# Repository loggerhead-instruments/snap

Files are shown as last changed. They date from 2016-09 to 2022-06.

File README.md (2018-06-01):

# SNAP
SNAP is an arduino-compatible audio datalogger board (designed for Teensy 3.x)

More information is at http://loggerhead.com

Files:
- snap: Main control and sensor recording
- cmd.pde: Reads recording settings from a script file
- wav.h: wav header
- rms: rms calculation

Software supports:
- duty cycle recording
- display
- button input for recording setup
- writing to microSD

## Updating Firmware

1.	Install Teensyduino from https://www.pjrc.com/teensy/loader.html
2.	Get latest hex file from appropriate repository
	https://github.com/loggerhead-instruments/snap/tree/master/hex
	To download the file, left-click on the file name, and then right click on the Raw button and select Save As link.
3.	Connect microUSB cable to small board on device. You may have to unscrew board.
4.	Run the Teensy Loader program.
5.	From File Menu, select Open HEX File
6.	Press the button on the board, or from Operation menu, select Program (you may have to turn off automatic mode).

To check whether the firmware has been updated, collect some data, and check the log files for the version date of the firmware.

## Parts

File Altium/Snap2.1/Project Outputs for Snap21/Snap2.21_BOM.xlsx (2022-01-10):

Comment | Description | DigiKey | Designator | Footprint | LibRef | Quantity | 100sets |  | NOTE
1uF | Ceramic Chip Capacitor - X7R, 1% |  | C1, C11, C16, C22 | 0402 | C0402 | 4 | $0.013 | $5.280
10uF | Tantalum Capacitor, 20%, 6.3V or better |  | C2, C6, C9, C14, C20 | Tant0805 | Tant0805 | 5 | $0.330 | $165.000 | TANT 10UF 6.3V 0805
0.1uF | Ceramic Chip Capacitor - X7R, 10% | 1276-1001-2-ND | C7, C8, C10, C13, C15, C17, C19, C21 | 0402 | C0402 | 8 | $0.013 | $10.560 | CL05B104KO5NNNC
0.01uF | Ceramic Chip Capacitor - X7R, 10% |  | C12, C18, C23 | 0402 | C0402 | 3 | $0.009 | $2.640
1.0uF | Ceramic Chip Capacitor - X7R, 1% |  | C24, C25, C26 | 0402 | C0402 | 3 | $0.013 | $3.960
LED_0603 | SML-D12M1WT86 or similar green | SML-D12M1WT86TR-ND | D1 | Diode0603 | LED_0603 | 1 | $0.121 | $12.100 | SML-D12M1WT86 5-7work days
Header 2 | 705530036 |  | P2 | HDR1X2 | Header 2 | 1 | $1.122 | $112.200 | 5-7work days
CoinCellHolder | BU2032SM-BT-GTR |  | P3 | CoinCellHolder | CoinCellHolder | 1 | $2.120 | $212.000 | 3-4work days
Slide switch OFF-ON header | EG1218 | EG1903-ND | P4 | HDR1X3 | Header 3 | 1 | $0.660 | $66.000
pushbutton | FSM2JSMATR | 450-1757-2-ND | P5, P7, P9 | SOP4 | pushbutton | 3 | $0.429 | $128.700 | 7-10work days
microSD | DM3D-SF | HR1941CT-ND | P6 | DM3D microSD | microSD Hirose | 1 | $1.892 | $189.200 | 5-7work days
Header 3 pin | 705530037 | WM4925-ND | P11 | HDR1X3 | Header 3 | 1 | $1.100 | $110.000 | 5-7work days
100k | Precision Thick Film Chip Resistor, 10 Ohm to 1M Ohm Range, 1% and 0.5% Tolerance, 0603 Size, 0.063 W |  | R1, R2 | 3-0603 | ERJ3RK | 2 | $0.009 | $1.760 | ERJ-3EKF1003V 100k 1% 0603,please confirm.
10k | Precision Thick Film Chip Resistor, 10 Ohm to 1M Ohm Range, 1% and 0.5% Tolerance, 0603 Size, 0.063 W |  | R3, R4, R5, R6 | 3-0603 | ERJ3RK | 4 | $0.009 | $3.520 | ERJ-3EKF1002V 10k 1% 0603,please confirm.
330X | Precision Thick Film Chip Resistor, 10 Ohm to 1M Ohm Range, 1% and 0.5% Tolerance, 0603 Size, 0.063 W |  | R7 | 3-0603 | ERJ3RK | 1 | $0.009 | $0.880 | ERJ-3EKF3300V 330R 1% 0603 ,please confirm.
4.7k | Precision Thick Film Chip Resistor, 10 Ohm to 1M Ohm Range, 1% and 0.5% Tolerance, 0603 Size, 0.063 W |  | R8, R9 | 3-0603 | ERJ3RK | 2 | $0.009 | $1.760 | ERJ-3EKF4701V 4.7k 1% 0603,please confirm.
Ideal Diode | LM66100 | 296-53540-1-ND | U1 | SC-70-6 | LM66100 | 0 | $0.264 | $0.000 | DO NOT PLACE
LP3985IM5-3.3 | Micropower, 150mA Low-Noise Ultra Low-Dropout CMOS Voltage Regulator | LP3985IM5-3.3/NOPBTR-ND | U3, U5, U6 | MF05A_N | LP3985IM5-3.3 | 3 | $0.330 | $99.000 | LP3985IM5-3.3/NOPB
SGTL5000 | SGTL5000 | SGTL5000XNAA3R2CT-ND | U4 | QFN32 | SGTL5000 | 1 | $1.760 | $176.000 | SGTL5000XNAA3R2
TLV70018DCKR | TLV70018DCKR | 296-32409-1-ND | U7 | TI-DCK5_V | TLV70018DCKR | 1 | $0.165 | $16.500
PMEG3050EP,115 | Shottky Diode | 1727-5317-1-ND | D2 |  |  | 1
 | P1 P8 不贴，D1 是绿色LED |  |  |  |  |  | 1KG
 |  |  |  |  |  |  |  | $409.420

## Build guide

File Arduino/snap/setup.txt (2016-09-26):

// Example setup.txt file

// Set time on power
TM 2016-06-06 12:00:00

// Enable IMU 100 Hz
IM 100.0

// MS Pressure
MP

// RGB light sensor
LS

// Rec duration
RD 30

// Rec interval
RI 30

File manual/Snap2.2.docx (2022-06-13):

# SNAP MANUAL

Multi-card Long-Term Underwater Acoustic Recorder

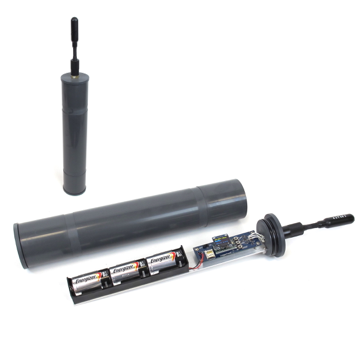
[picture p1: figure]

Manual v1.0

Updated 13 June 2022

www.loggerhead.com

# Overview

Hardware

Snap is datalogger designed for collecting large amounts of underwater acoustic recordings. Setup is designed to run through a simple button interface with a display. No PC is needed to setup and deploy the Snap.

- HTI-96-min Hydrophone
- 3 Alkaline D-Cell Bateries
- 1 microSD cards formatted as FAT32

Software

Snap stores data directly as audio wav files.

Any audio analysis software (Adobe Audition, Cornell Raven, MATLAB, R, Python) will work with these files.

For noise analysis, the open source Manta software is designed to run with audio files collected by the Snap.

https://bitbucket.org/CLO-BRP/manta-wiki/wiki/Home

Setting up Snap for Deployment

See the online video for a tutorial on setting up the Snap

Step 1. Prepare microSD card. microSD cards larger than 32 GB need to be formatted as FAT32. Appendix 1 describes software that can be used to do this on Windows PCs.

The card shipped with the Snap from Loggerhead has already been formatted as FAT32.

Step 2. O-rings. Clean and grease o-rings with silicone grease and insert into the groove on the ring. The o-rings (-228) are McMaster part number: https://www.mcmaster.com/9452K66/

Step 3. Turn on power switch.

The Snap has battery holders for 1 set of 3 D-cell alkaline batteries.

Do not use NiMH or Lithium batteries.

Alkaline batteries can be packed in luggage on an airplane and can be bought in most field locations. When traveling to remote areas it is a good idea to bring new batteries.

The microSD cards will be scanned for free memory. There MUST be a card in slot 1.

Use buttons to change settings

Enter: Used to move through menu settings and accept changes.

UP/DN: Used to change values.

Display Setting | Description
UP+DN->Rec | Hold down UP + DN to start Press Enter to change settings UP+DN may also be used to stop a recording in progress.
Rec: | Record duration in seconds
Slp: | Sleep duration in seconds. This is the time from the END of one recording to the START of the next recording.
Year: | Year
Month: | Month
Day: | Day of month
Hour: | Hour (24 hour time)
Minute: | Minute
Second: | Second
SF: | Sampling Frequency (in Hz): The sampling rate of the Snap can be changed depending on the frequency of interest (the sampling rate needs to be at least twice as high as the highest frequency you want to record). E.g. 48 kHz sampling frequency can record sounds up to 24 kHz.

Step 5. Start Recording. Hold down the UP and DN buttons at the same time to start recording. If this is not done, the recorder will automatically start after 15 minutes. A red LED in the end of the hydrophone will illuminate while a recording is in process (if you are using the HTI-96-min).

Step 6. Close lid. Snap the lids into place. The water pressure will hold the lid in place underwater. If you are deploying where the water is warm, it is best to open the Snap and close the lid outside just prior to deployment. Since cold air expands when heated, it is best not to close them up inside an air-conditioned room and then deploy in water that is warmer than the air-conditioned room.

Step 7. Deploy. The Snap can be attached to a bottom mount (e.g. cinder block) or subsurface line using hose clamps or large tie wraps.

Retrieval

Upon retrieval, open the top lid by pushing up on opposite sides of the lip, and pull out the Snap board. If a recording is still happening (red hydrophone LED on and green LED on board flashing), hold down the UP + DN buttons at the same time. This will properly close the file before stopping recording. Then switch off the board and remove the microSD card.

# Appendix I

Formatting SD card with EaseUS Partition Master for Cards Larger than 32 GB

32 GB cards can be formatted as FAT32 in Windows with standard re-formatting. New 32 GB cards will come formatted as FAT32 (you don’t need to do anything).

EaseUS Partition Master Instructions

https://www.easeus.com/download/epmf-download.html

1. Click on the drive with the microSD card.
2. Click Format button the right
3. In pop-up dialog box Change cluster size to 64 KB. Click OK
4. On top of screen click on Execute 1 Operation

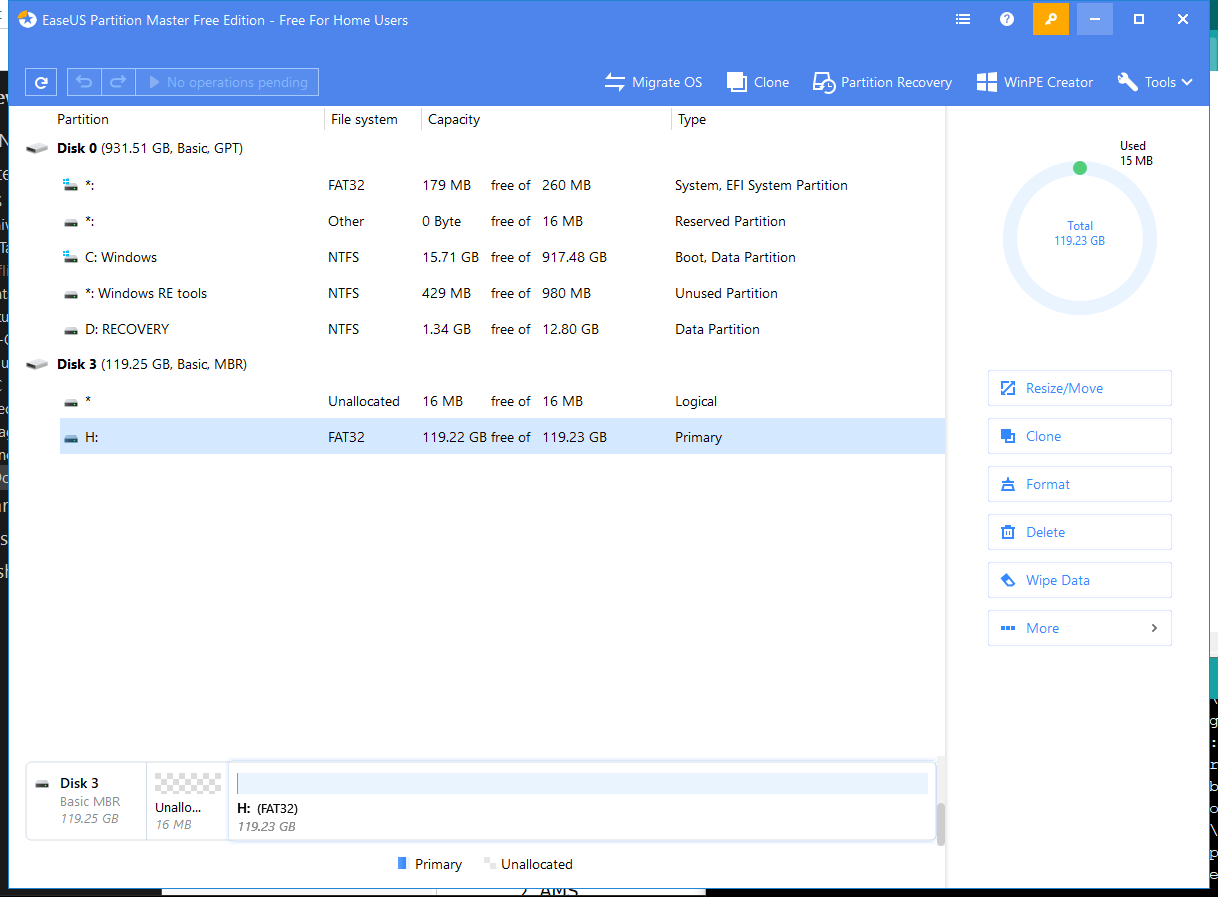
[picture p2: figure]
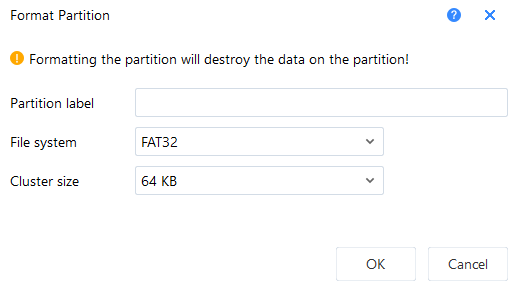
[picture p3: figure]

Appendix II

Two settings can only be changed by placing a text file on the microSD card, placing it in the Snap, and turning the Snap on. The Snap ships with defaults that work in most situations.

setup.txt Commands

All commands are optional. Default column lists values if no setting in setup.txt file. Record duration and record interval can be set through the button interface.

Command | Function | Default | Example | Setup.txt example
SG | Hydrophone system gain. See table for dB gains associated with different settings. | 4 | Set gain to setting ‘10’, which corresponds to 11.1 dB gain | SG 10
ND | Remove DC from audio. Turning on increases electrical noise | Off | Turn on feature to remove DC from audio | ND

# HTI Hydrophone and Recording Gain

The Snap uses a hydrophone manufactured by High-Tech Inc. The sensitivity of the hydrophone will be on a specification sheet included with the shipment (typically -170 dBV/uPa or -180 dBV/uPa).

The hydrophone has a red LED in the end to indicate when it is getting power. This will only be turned on during startup and recording. The hydrophone red LED will be off when sleeping.

The A/D converter gain can be changed through the setup.txt file. The default is setting 4. The setting can be changed with SG command in setup.txt. The actual setting that was used is stored to the log.txt file.

Setting | Clip Level (peak-peak) | Clip Level (peak) | Gain (dB)
0 | 3.12 | 1.56 | -3.9
1 | 2.63 | 1.315 | -2.4
2 | 2.22 | 1.11 | -0.9
3 | 1.87 | 0.935 | 0.6
4 | 1.58 | 0.79 | 2.0
5 | 1.33 | 0.665 | 3.5
6 | 1.11 | 0.555 | 5.1
7 | 0.94 | 0.47 | 6.6
8 | 0.79 | 0.395 | 8.1
9 | 0.67 | 0.335 | 9.5
10 | 0.56 | 0.28 | 11.1
11 | 0.48 | 0.24 | 12.4
12 | 0.4 | 0.2 | 14.0
13 | 0.34 | 0.17 | 15.4
14 | 0.29 | 0.145 | 16.8
15 | 0.24 | 0.12 | 18.4

Snap Manual 18

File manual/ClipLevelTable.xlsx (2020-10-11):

SG | A/D Converter Gain |  | Clip Level | Clip Level -180 dB hydrophone | Clip Level -170 dB hydrophone | Clip Level -210 dB hydrophone
 |  |  | Peak (V) | Peak dB re 1uPa | Peak dB re 1uPa | Peak dB re 1uPa
 | Linear | dB |  | dB | dB | dB
0 | 0.6382634862 | -3.9 | 3.12 | 183.9 | 173.9 | 213.9
1 | 0.758577575 | -2.4 | 2.63 | 182.4 | 172.4 | 212.4
2 | 0.9015711376 | -0.9 | 2.22 | 180.9 | 170.9 | 210.9
3 | 1.071519305 | 0.6 | 1.87 | 179.4 | 169.4 | 209.4
4 | 1.258925412 | 2 | 1.58 | 178.0 | 168.0 | 208.0
5 | 1.496235656 | 3.5 | 1.33 | 176.5 | 166.5 | 206.5
6 | 1.798870915 | 5.1 | 1.11 | 174.9 | 164.9 | 204.9
7 | 2.13796209 | 6.6 | 0.94 | 173.4 | 163.4 | 203.4
8 | 2.540972706 | 8.1 | 0.79 | 171.9 | 161.9 | 201.9
9 | 2.985382619 | 9.5 | 0.67 | 170.5 | 160.5 | 200.5
10 | 3.589219346 | 11.1 | 0.56 | 168.9 | 158.9 | 198.9
11 | 4.168693835 | 12.4 | 0.48 | 167.6 | 157.6 | 197.6
12 | 5.011872336 | 14 | 0.4 | 166.0 | 156.0 | 196.0
13 | 5.888436554 | 15.4 | 0.34 | 164.6 | 154.6 | 194.6
14 | 6.918309709 | 16.8 | 0.29 | 163.2 | 153.2 | 193.2
15 | 8.317637711 | 18.4 | 0.24 | 161.6 | 151.6 | 191.6

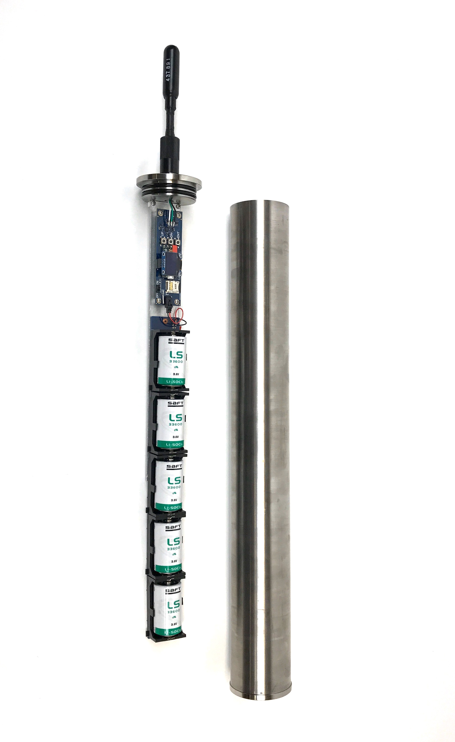
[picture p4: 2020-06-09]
manual/titanium Snap.jpeg

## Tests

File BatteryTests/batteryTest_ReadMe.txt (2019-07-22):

July 2019

Test with LSH20 and LS33600
Test in refrigerator
1 cell only

Conclusion:
With 1 cell, LSH20 lasts longer.
May not be as much difference with 5 cells in parallel because of reduced current draw.
But, for cold water, use LSH20

For power calculations: assume 10 Ah capacity

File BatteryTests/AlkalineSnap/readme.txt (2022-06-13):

5/30/2022

Running at 300 kHz in freezer with 512 GB Samsung green microSD

Get about 2 good days of recordings before hydrophone starts to get spiky noise.
Amazon Basics D-cells

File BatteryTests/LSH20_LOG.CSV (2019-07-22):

filename | ID | gain (dB) | Voltage | Version
20190701T141040.wav | 0423322908248198 | 0.00 | 3.66 | 2019-05-28
20190701T141240.wav | 0423322908248198 | 0.00 | 3.70 | 2019-05-28
20190701T141440.wav | 0423322908248198 | 0.00 | 3.65 | 2019-05-28
20190701T141640.wav | 0423322908248198 | 0.00 | 3.72 | 2019-05-28
20190701T141840.wav | 0423322908248198 | 0.00 | 3.74 | 2019-05-28
20190701T142040.wav | 0423322908248198 | 0.00 | 3.73 | 2019-05-28
20190701T142240.wav | 0423322908248198 | 0.00 | 3.73 | 2019-05-28
20190701T142440.wav | 0423322908248198 | 0.00 | 3.72 | 2019-05-28
20190701T142640.wav | 0423322908248198 | 0.00 | 3.75 | 2019-05-28
20190701T142840.wav | 0423322908248198 | 0.00 | 3.75 | 2019-05-28
20190701T143040.wav | 0423322908248198 | 0.00 | 3.67 | 2019-05-28
20190701T143240.wav | 0423322908248198 | 0.00 | 3.72 | 2019-05-28
20190701T143440.wav | 0423322908248198 | 0.00 | 3.69 | 2019-05-28
20190701T143640.wav | 0423322908248198 | 0.00 | 3.73 | 2019-05-28
20190701T143840.wav | 0423322908248198 | 0.00 | 3.72 | 2019-05-28
20190701T144040.wav | 0423322908248198 | 0.00 | 3.78 | 2019-05-28
20190701T144240.wav | 0423322908248198 | 0.00 | 3.73 | 2019-05-28
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

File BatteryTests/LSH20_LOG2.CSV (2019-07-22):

filename | ID | gain (dB) | Voltage | Version
20190708T152140.wav | 0423322908248198 | 2.05 | 3.43 | 2019-05-28
20190708T152340.wav | 0423322908248198 | 2.05 | 3.55 | 2019-05-28
20190708T152540.wav | 0423322908248198 | 2.05 | 3.61 | 2019-05-28
20190708T152740.wav | 0423322908248198 | 2.05 | 3.62 | 2019-05-28
20190708T152940.wav | 0423322908248198 | 2.05 | 3.68 | 2019-05-28
20190708T153140.wav | 0423322908248198 | 2.05 | 3.73 | 2019-05-28
20190708T153340.wav | 0423322908248198 | 2.05 | 3.62 | 2019-05-28
20190708T153540.wav | 0423322908248198 | 2.05 | 3.66 | 2019-05-28
20190708T153740.wav | 0423322908248198 | 2.05 | 3.61 | 2019-05-28
20190708T153940.wav | 0423322908248198 | 2.05 | 3.69 | 2019-05-28
20190708T154140.wav | 0423322908248198 | 2.05 | 3.64 | 2019-05-28
20190708T154340.wav | 0423322908248198 | 2.05 | 3.63 | 2019-05-28
20190708T154540.wav | 0423322908248198 | 2.05 | 3.63 | 2019-05-28
20190708T154740.wav | 0423322908248198 | 2.05 | 3.68 | 2019-05-28
20190708T154940.wav | 0423322908248198 | 2.05 | 3.53 | 2019-05-28
20190708T155140.wav | 0423322908248198 | 2.05 | 3.57 | 2019-05-28
20190708T155340.wav | 0423322908248198 | 2.05 | 3.51 | 2019-05-28
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

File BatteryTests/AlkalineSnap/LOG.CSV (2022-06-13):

filename | Voltage | Version | Notes on when things start to get bad
20220524T181730_2614231121589262_2.0.wav | 4.46 | 1/5/2022 | good recording
20220524T182730_2614231121589262_2.0.wav | 4.54 | 1/5/2022
20220524T183730_2614231121589262_2.0.wav | 4.54 | 1/5/2022
20220524T184730_2614231121589262_2.0.wav | 4.51 | 1/5/2022
20220524T185730_2614231121589262_2.0.wav | 4.5 | 1/5/2022
20220524T190730_2614231121589262_2.0.wav | 4.48 | 1/5/2022
20220524T191730_2614231121589262_2.0.wav | 4.43 | 1/5/2022
20220524T192730_2614231121589262_2.0.wav | 4.47 | 1/5/2022
20220524T193730_2614231121589262_2.0.wav | 4.46 | 1/5/2022
20220524T194730_2614231121589262_2.0.wav | 4.48 | 1/5/2022
20220524T195730_2614231121589262_2.0.wav | 4.44 | 1/5/2022
20220524T200731_2614231121589262_2.0.wav | 4.45 | 1/5/2022
20220524T201731_2614231121589262_2.0.wav | 4.43 | 1/5/2022
20220524T202731_2614231121589262_2.0.wav | 4.44 | 1/5/2022
20220524T203731_2614231121589262_2.0.wav | 4.44 | 1/5/2022
20220524T204731_2614231121589262_2.0.wav | 4.36 | 1/5/2022
20220524T205731_2614231121589262_2.0.wav | 4.39 | 1/5/2022
20220524T210731_2614231121589262_2.0.wav | 4.39 | 1/5/2022
20220524T211731_2614231121589262_2.0.wav | 4.37 | 1/5/2022
20220524T212731_2614231121589262_2.0.wav | 4.35 | 1/5/2022
20220524T213731_2614231121589262_2.0.wav | 4.38 | 1/5/2022
20220524T214731_2614231121589262_2.0.wav | 4.34 | 1/5/2022
20220524T215731_2614231121589262_2.0.wav | 4.38 | 1/5/2022
20220524T220731_2614231121589262_2.0.wav | 4.37 | 1/5/2022
20220524T221731_2614231121589262_2.0.wav | 4.36 | 1/5/2022
20220524T222731_2614231121589262_2.0.wav | 4.34 | 1/5/2022
20220524T223731_2614231121589262_2.0.wav | 4.36 | 1/5/2022
20220524T224731_2614231121589262_2.0.wav | 4.3 | 1/5/2022
20220524T225731_2614231121589262_2.0.wav | 4.3 | 1/5/2022
20220524T230731_2614231121589262_2.0.wav | 4.29 | 1/5/2022
20220524T231731_2614231121589262_2.0.wav | 4.32 | 1/5/2022
20220524T232731_2614231121589262_2.0.wav | 4.29 | 1/5/2022
20220524T233731_2614231121589262_2.0.wav | 4.32 | 1/5/2022
20220524T234731_2614231121589262_2.0.wav | 4.34 | 1/5/2022
20220524T235731_2614231121589262_2.0.wav | 4.31 | 1/5/2022
20220525T000731_2614231121589262_2.0.wav | 4.3 | 1/5/2022
20220525T001731_2614231121589262_2.0.wav | 4.3 | 1/5/2022
20220525T002731_2614231121589262_2.0.wav | 4.26 | 1/5/2022
20220525T003732_2614231121589262_2.0.wav | 4.26 | 1/5/2022
20220525T004732_2614231121589262_2.0.wav | 4.24 | 1/5/2022
20220525T005732_2614231121589262_2.0.wav | 4.27 | 1/5/2022
20220525T010732_2614231121589262_2.0.wav | 4.26 | 1/5/2022
20220525T011732_2614231121589262_2.0.wav | 4.3 | 1/5/2022
20220525T012732_2614231121589262_2.0.wav | 4.25 | 1/5/2022
20220525T013732_2614231121589262_2.0.wav | 4.3 | 1/5/2022
20220525T014732_2614231121589262_2.0.wav | 4.26 | 1/5/2022
20220525T015732_2614231121589262_2.0.wav | 4.26 | 1/5/2022
20220525T020732_2614231121589262_2.0.wav | 4.25 | 1/5/2022
20220525T021732_2614231121589262_2.0.wav | 4.23 | 1/5/2022
20220525T022732_2614231121589262_2.0.wav | 4.24 | 1/5/2022
20220525T023732_2614231121589262_2.0.wav | 4.26 | 1/5/2022
20220525T024732_2614231121589262_2.0.wav | 4.27 | 1/5/2022
20220525T025732_2614231121589262_2.0.wav | 4.24 | 1/5/2022
20220525T030732_2614231121589262_2.0.wav | 4.24 | 1/5/2022
20220525T031732_2614231121589262_2.0.wav | 4.23 | 1/5/2022
20220525T032732_2614231121589262_2.0.wav | 4.25 | 1/5/2022
20220525T033732_2614231121589262_2.0.wav | 4.24 | 1/5/2022
20220525T034732_2614231121589262_2.0.wav | 4.25 | 1/5/2022
20220525T035732_2614231121589262_2.0.wav | 4.23 | 1/5/2022
20220525T040732_2614231121589262_2.0.wav | 4.24 | 1/5/2022
20220525T041733_2614231121589262_2.0.wav | 4.24 | 1/5/2022
20220525T042733_2614231121589262_2.0.wav | 4.21 | 1/5/2022
20220525T043733_2614231121589262_2.0.wav | 4.22 | 1/5/2022
20220525T044733_2614231121589262_2.0.wav | 4.22 | 1/5/2022
20220525T045733_2614231121589262_2.0.wav | 4.22 | 1/5/2022
20220525T050733_2614231121589262_2.0.wav | 4.21 | 1/5/2022
20220525T051733_2614231121589262_2.0.wav | 4.25 | 1/5/2022
20220525T052733_2614231121589262_2.0.wav | 4.24 | 1/5/2022
20220525T053733_2614231121589262_2.0.wav | 4.24 | 1/5/2022
20220525T054733_2614231121589262_2.0.wav | 4.23 | 1/5/2022
20220525T055733_2614231121589262_2.0.wav | 4.22 | 1/5/2022
20220525T060733_2614231121589262_2.0.wav | 4.22 | 1/5/2022
20220525T061733_2614231121589262_2.0.wav | 4.22 | 1/5/2022
20220525T062733_2614231121589262_2.0.wav | 4.22 | 1/5/2022
20220525T063733_2614231121589262_2.0.wav | 4.23 | 1/5/2022
20220525T064733_2614231121589262_2.0.wav | 4.19 | 1/5/2022
20220525T065733_2614231121589262_2.0.wav | 4.22 | 1/5/2022
20220525T070733_2614231121589262_2.0.wav | 4.23 | 1/5/2022
20220525T071733_2614231121589262_2.0.wav | 4.2 | 1/5/2022
20220525T072733_2614231121589262_2.0.wav | 4.24 | 1/5/2022
20220525T073734_2614231121589262_2.0.wav | 4.22 | 1/5/2022
20220525T074734_2614231121589262_2.0.wav | 4.23 | 1/5/2022
20220525T075734_2614231121589262_2.0.wav | 4.23 | 1/5/2022
20220525T080734_2614231121589262_2.0.wav | 4.24 | 1/5/2022
20220525T081734_2614231121589262_2.0.wav | 4.19 | 1/5/2022
20220525T082734_2614231121589262_2.0.wav | 4.18 | 1/5/2022
20220525T083734_2614231121589262_2.0.wav | 4.16 | 1/5/2022
20220525T084734_2614231121589262_2.0.wav | 4.16 | 1/5/2022
20220525T085734_2614231121589262_2.0.wav | 4.19 | 1/5/2022
20220525T090734_2614231121589262_2.0.wav | 4.18 | 1/5/2022
20220525T091734_2614231121589262_2.0.wav | 4.18 | 1/5/2022
20220525T092734_2614231121589262_2.0.wav | 4.2 | 1/5/2022
20220525T093734_2614231121589262_2.0.wav | 4.19 | 1/5/2022
20220525T094734_2614231121589262_2.0.wav | 4.19 | 1/5/2022
20220525T095734_2614231121589262_2.0.wav | 4.18 | 1/5/2022
20220525T100734_2614231121589262_2.0.wav | 4.2 | 1/5/2022
20220525T101734_2614231121589262_2.0.wav | 4.19 | 1/5/2022
20220525T102734_2614231121589262_2.0.wav | 4.17 | 1/5/2022
20220525T103734_2614231121589262_2.0.wav | 4.16 | 1/5/2022
20220525T104735_2614231121589262_2.0.wav | 4.12 | 1/5/2022
20220525T105735_2614231121589262_2.0.wav | 4.15 | 1/5/2022
20220525T110735_2614231121589262_2.0.wav | 4.15 | 1/5/2022
20220525T111735_2614231121589262_2.0.wav | 4.2 | 1/5/2022
20220525T112735_2614231121589262_2.0.wav | 4.18 | 1/5/2022
20220525T113735_2614231121589262_2.0.wav | 4.19 | 1/5/2022
20220525T114735_2614231121589262_2.0.wav | 4.17 | 1/5/2022
20220525T115735_2614231121589262_2.0.wav | 4.19 | 1/5/2022
20220525T120735_2614231121589262_2.0.wav | 4.13 | 1/5/2022
20220525T121735_2614231121589262_2.0.wav | 4.14 | 1/5/2022
20220525T122735_2614231121589262_2.0.wav | 4.1 | 1/5/2022
20220525T123735_2614231121589262_2.0.wav | 4.14 | 1/5/2022
20220525T124735_2614231121589262_2.0.wav | 4.13 | 1/5/2022
20220525T125735_2614231121589262_2.0.wav | 4.16 | 1/5/2022
20220525T130735_2614231121589262_2.0.wav | 4.15 | 1/5/2022
20220525T131736_2614231121589262_2.0.wav | 4.15 | 1/5/2022
20220525T132736_2614231121589262_2.0.wav | 4.15 | 1/5/2022
20220525T133736_2614231121589262_2.0.wav | 4.14 | 1/5/2022
20220525T134736_2614231121589262_2.0.wav | 4.12 | 1/5/2022
20220525T135736_2614231121589262_2.0.wav | 4.16 | 1/5/2022
20220525T140736_2614231121589262_2.0.wav | 4.14 | 1/5/2022
20220525T141736_2614231121589262_2.0.wav | 4.15 | 1/5/2022
20220525T142736_2614231121589262_2.0.wav | 4.11 | 1/5/2022
20220525T143736_2614231121589262_2.0.wav | 4.09 | 1/5/2022
20220525T144736_2614231121589262_2.0.wav | 4.09 | 1/5/2022
20220525T145736_2614231121589262_2.0.wav | 4.09 | 1/5/2022
20220525T150736_2614231121589262_2.0.wav | 4.06 | 1/5/2022
20220525T151736_2614231121589262_2.0.wav | 4.12 | 1/5/2022
20220525T152736_2614231121589262_2.0.wav | 4.13 | 1/5/2022
20220525T153736_2614231121589262_2.0.wav | 4.14 | 1/5/2022
20220525T154736_2614231121589262_2.0.wav | 4.14 | 1/5/2022
20220525T155736_2614231121589262_2.0.wav | 4.11 | 1/5/2022
20220525T160737_2614231121589262_2.0.wav | 4.11 | 1/5/2022
20220525T161737_2614231121589262_2.0.wav | 4.12 | 1/5/2022
20220525T162737_2614231121589262_2.0.wav | 4.07 | 1/5/2022
20220525T163737_2614231121589262_2.0.wav | 4.12 | 1/5/2022
20220525T164737_2614231121589262_2.0.wav | 4.06 | 1/5/2022
20220525T165737_2614231121589262_2.0.wav | 4.11 | 1/5/2022
20220525T170737_2614231121589262_2.0.wav | 4.08 | 1/5/2022
20220525T171737_2614231121589262_2.0.wav | 4.13 | 1/5/2022
20220525T172737_2614231121589262_2.0.wav | 4.13 | 1/5/2022
20220525T173737_2614231121589262_2.0.wav | 4.16 | 1/5/2022
20220525T174737_2614231121589262_2.0.wav | 4.15 | 1/5/2022
20220525T175737_2614231121589262_2.0.wav | 4.11 | 1/5/2022
20220525T180737_2614231121589262_2.0.wav | 4.08 | 1/5/2022
20220525T181737_2614231121589262_2.0.wav | 4.1 | 1/5/2022
20220525T182738_2614231121589262_2.0.wav | 4.07 | 1/5/2022
20220525T183738_2614231121589262_2.0.wav | 4.1 | 1/5/2022
20220525T184738_2614231121589262_2.0.wav | 4.09 | 1/5/2022
20220525T185738_2614231121589262_2.0.wav | 4.07 | 1/5/2022
20220525T190738_2614231121589262_2.0.wav | 4.09 | 1/5/2022
20220525T191738_2614231121589262_2.0.wav | 4.11 | 1/5/2022
20220525T192738_2614231121589262_2.0.wav | 4.11 | 1/5/2022
20220525T193738_2614231121589262_2.0.wav | 4.11 | 1/5/2022
20220525T194738_2614231121589262_2.0.wav | 4.11 | 1/5/2022
20220525T195738_2614231121589262_2.0.wav | 4.12 | 1/5/2022
20220525T200738_2614231121589262_2.0.wav | 4.11 | 1/5/2022
20220525T201738_2614231121589262_2.0.wav | 4.1 | 1/5/2022
20220525T202738_2614231121589262_2.0.wav | 4.08 | 1/5/2022
20220525T203739_2614231121589262_2.0.wav | 4.07 | 1/5/2022
20220525T204739_2614231121589262_2.0.wav | 4.1 | 1/5/2022
20220525T205739_2614231121589262_2.0.wav | 4.11 | 1/5/2022
20220525T210739_2614231121589262_2.0.wav | 4.08 | 1/5/2022
20220525T211739_2614231121589262_2.0.wav | 4.12 | 1/5/2022
20220525T212739_2614231121589262_2.0.wav | 4.11 | 1/5/2022
20220525T213739_2614231121589262_2.0.wav | 4.09 | 1/5/2022
20220525T214739_2614231121589262_2.0.wav | 4.11 | 1/5/2022
20220525T215739_2614231121589262_2.0.wav | 4.1 | 1/5/2022
20220525T220739_2614231121589262_2.0.wav | 4.12 | 1/5/2022
20220525T221739_2614231121589262_2.0.wav | 4.09 | 1/5/2022
20220525T222739_2614231121589262_2.0.wav | 4.1 | 1/5/2022
20220525T223739_2614231121589262_2.0.wav | 4.09 | 1/5/2022
20220525T224740_2614231121589262_2.0.wav | 4.05 | 1/5/2022
20220525T225740_2614231121589262_2.0.wav | 4.12 | 1/5/2022
20220525T230740_2614231121589262_2.0.wav | 4.05 | 1/5/2022
20220525T231740_2614231121589262_2.0.wav | 4.03 | 1/5/2022
20220525T232740_2614231121589262_2.0.wav | 4.1 | 1/5/2022
20220525T233740_2614231121589262_2.0.wav | 4.11 | 1/5/2022
20220525T234740_2614231121589262_2.0.wav | 4.11 | 1/5/2022
20220525T235740_2614231121589262_2.0.wav | 4.11 | 1/5/2022
20220526T000740_2614231121589262_2.0.wav | 4.09 | 1/5/2022
20220526T001740_2614231121589262_2.0.wav | 4.06 | 1/5/2022
20220526T002740_2614231121589262_2.0.wav | 4.05 | 1/5/2022
20220526T003741_2614231121589262_2.0.wav | 4.07 | 1/5/2022
20220526T004741_2614231121589262_2.0.wav | 4.07 | 1/5/2022
20220526T005741_2614231121589262_2.0.wav | 4.03 | 1/5/2022
20220526T010742_2614231121589262_2.0.wav | 3.98 | 1/5/2022
20220526T011742_2614231121589262_2.0.wav | 4.03 | 1/5/2022
20220526T012743_2614231121589262_2.0.wav | 4.03 | 1/5/2022
20220526T013743_2614231121589262_2.0.wav | 4.07 | 1/5/2022
20220526T014743_2614231121589262_2.0.wav | 4.08 | 1/5/2022
20220526T015743_2614231121589262_2.0.wav | 4.07 | 1/5/2022
20220526T020743_2614231121589262_2.0.wav | 4.12 | 1/5/2022
20220526T021743_2614231121589262_2.0.wav | 4.02 | 1/5/2022
20220526T022743_2614231121589262_2.0.wav | 4 | 1/5/2022
20220526T023743_2614231121589262_2.0.wav | 4.06 | 1/5/2022
20220526T024743_2614231121589262_2.0.wav | 3.99 | 1/5/2022
20220526T025743_2614231121589262_2.0.wav | 4.01 | 1/5/2022
20220526T030744_2614231121589262_2.0.wav | 4.01 | 1/5/2022
20220526T031744_2614231121589262_2.0.wav | 4.04 | 1/5/2022
20220526T032744_2614231121589262_2.0.wav | 4.03 | 1/5/2022
20220526T033744_2614231121589262_2.0.wav | 4.02 | 1/5/2022
20220526T034744_2614231121589262_2.0.wav | 4.07 | 1/5/2022
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

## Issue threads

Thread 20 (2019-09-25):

### ISSUE TITLE
Double frequency issue when recording

### ISSUE THREAD

**Issue by brivbl** [loggerhead-instruments/snap#20]
Hello,

I tried compiling the source code on a loggerhead snap card to record a 1kHz sine signal. When I analyze the output .wav file with audacity, I get a 2kHz sine signal. (.wav header parameters were unchanged, 1 channel, 16 bits per sample, 44.1kHz samplerate).

But when I use the latest hex file available, I can get a 1kHz .wav signal without any problem.

Do you have an idea where this issue can come from ? I tried re-installing the teensy Audio.h library, but no success.

thank you.

**Comment by davidallenmann** [comment]
Are you using the audio library from here:
https://github.com/loggerhead-instruments/libraries/tree/master/snap_libraries

**Comment by WMXZ-EU** [comment]
Could you also indicate, which F_CPU you were setting for compilation?

**Comment by brivbl** [comment]
Thanks for the library suggestion, I just installed them now and it works perfectly.

Also I was using the 72 MHz compilation frequency.

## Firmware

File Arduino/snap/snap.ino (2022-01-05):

//
// SNAP acoustic recorder
//
// Loggerhead Instruments
// 2016-2022
// David Mann
// 
// Modified from PJRC audio code
// http://www.pjrc.com/store/teensy3_audio.html
//
// Compile with 96 MHz Fastest

// Modified by WMXZ 15-05-2018 for SdFS anf multiple sampling frequencies
// Optionally uses SdFS from Bill Greiman https://github.com/greiman/SdFs; but has higher current draw in sleep

char codeVersion[12] = "2022-01-05";
static boolean printDiags = 1;  // 1: serial print diagnostics; 0: no diagnostics

#define USE_SDFS 0  // to be used for exFAT but works also for FAT16/32
#define MQ 100 // to be used with LHI record queue (modified local version)
//#define USE_LONG_FILE_NAMES

#include "LHI_record_queue.h"
#include "control_sgtl5000.h"

//#include <SerialFlash.h>
#if USE_SDFS==0
  #include "input_i2s.h"
//  #include "LHI_record_queue.h"
//  #include "control_sgtl5000.h"
#else
  #include <Audio.h>  //this also includes SD.h from lines 89 & 90
#endif
#include <Wire.h>
#include <SPI.h>
#if USE_SDFS==1
  #include "SdFs.h"
#else
  #include "SdFat.h"
#endif
#include "amx32.h"

#include <Snooze.h>  //using https://github.com/duff2013/Snooze; uncomment line 62 #define USE_HIBERNATE

#include <TimeLib.h>
#include <Adafruit_GFX.h>
#include <Adafruit_SSD1306.h>
#include <EEPROM.h>
//#include <TimerOne.h>

#define CPU_RESTART_ADDR (uint32_t *)0xE000ED0C
#define CPU_RESTART_VAL 0x5FA0004
#define CPU_RESTART (*CPU_RESTART_ADDR = CPU_RESTART_VAL);

#define OLED_RESET -1
Adafruit_SSD1306 display(OLED_RESET);
#define BOTTOM 55

// set this to the hardware serial port you wish to use
#define HWSERIAL Serial1

#define NREC 32 // increase disk buffer to speed up disk access

static uint32_t myID[2];

unsigned long baud = 115200;

#define SECONDS_IN_MINUTE 60
#define SECONDS_IN_HOUR 3600
#define SECONDS_IN_DAY 86400
#define SECONDS_IN_YEAR 31536000
#define SECONDS_IN_LEAP 31622400

#define MODE_NORMAL 0
#define MODE_DIEL 1

// GUItool: begin automatically generated code
AudioInputI2S            i2s2;           //xy=105,63
LHIRecordQueue           queue1;         //xy=281,63
AudioConnection          patchCord1(i2s2, 0, queue1, 0);
AudioControlSGTL5000     sgtl5000_1;     //xy=265,212
// GUItool: end automatically generated code

const int myInput = AUDIO_INPUT_LINEIN;
unsigned int gainSetting = 4; //default gain setting; can be overridden in setup file
int noDC = 1; // 0 = freezeDC offset; 1 = remove DC offset

// Pin Assignments
const int hydroPowPin = 2;
const int sgtlEn = 6;

// Snap
const int UP = 4;
const int DOWN = 3;  // new board pin
//const int DOWN = 5; // old board down pin
const int SELECT = 8;
const int displayPow = 20;
#define ledGreen 17
const int SDSW = 0;
#define vSense A7 
//const int vSense = A14;  // moved to Pin 21 (A7) for X1

// Pins used by audio shield
// https://www.pjrc.com/store/teensy3_audio.html
// MEMCS 6
// MOSI 7
// BCLK 9
// SDCS 10
// MCLK 11
// MISO 12
// RX 13
// SCLK 14
// VOL 15
// SDA 18
// SCL 19
// TX 22
// LRCLK 23

// Remember which mode we're doing
int mode = 0;  // 0=stopped, 1=recording, 2=playing
time_t startTime;
time_t stopTime;
time_t t;
time_t burnTime;
byte startHour, startMinute, endHour, endMinute; //used in Diel mode

boolean audioFlag = 1;

boolean LEDSON=1;
boolean introperiod=1;  //flag for introductory period; used for keeping LED on for a little while

int32_t lhi_fsamps[9] = {8000, 16000, 32000, 44100, 48000, 96000, 200000, 250000, 300000};
#define I_SAMP 9
int isf = 3;
float audio_srate = lhi_fsamps[isf];//44100.0;

//WMXZ float audioIntervalSec = 256.0 / audio_srate; //buffer interval in seconds
//WMXZ unsigned int audioIntervalCount = 0;
float gainDb;

int recMode = MODE_NORMAL;
long rec_dur = 10;
long rec_int = 30;
int wakeahead = 5;  //wake from snooze to give hydrophone and camera time to power up
int snooze_hour;
int snooze_minute;
int snooze_second;
int buf_count;
long nbufs_per_file;
boolean settingsChanged = 0;

long file_count;
char filename[60];
char dirname[20];
int folderMonth;

SnoozeAlarm alarm;
SnoozeAudio snooze_audio;
SnoozeBlock config_teensy32(snooze_audio, alarm);


// The file where data is recorded
#if USE_SDFS==1
  FsFile frec;
  SdFs sd;
#else
  File frec;
  SdFat sd;
  //SdFile file; // not used(WMXZ)
#endif

typedef struct {
    char    rId[4];
    unsigned int rLen;
    char    wId[4];
    char    fId[4];
    unsigned int    fLen;
    unsigned short nFormatTag;
    unsigned short nChannels;
    unsigned int nSamplesPerSec;
    unsigned int nAvgBytesPerSec;
    unsigned short nBlockAlign;
    unsigned short  nBitsPerSamples;
    char    dId[4];
    unsigned int    dLen;
} HdrStruct;

HdrStruct wav_hdr;

unsigned char prev_dtr = 0;


void setup() {
  Serial.begin(baud);
  delay(500);


  Serial.println(RTC_TSR);
  Serial.println(RTC_TSR);
  Serial.println(RTC_TSR);

  RTC_CR = 0; // disable RTC
  delay(100);
  Serial.println(RTC_CR,HEX);
  // change capacitance to 26 pF (12.5 pF load capacitance)
  RTC_CR = RTC_CR_SC16P | RTC_CR_SC8P | RTC_CR_SC2P; 
  delay(100);
  RTC_CR = RTC_CR_SC16P | RTC_CR_SC8P | RTC_CR_SC2P | RTC_CR_OSCE;
  delay(100);

  Serial.println(RTC_SR,HEX);
  Serial.println(RTC_CR,HEX);
  Serial.println(RTC_LR,HEX);

  Serial.println(RTC_TSR);
  delay(1000);
  Serial.println(RTC_TSR);
  delay(1000);
  Serial.println(RTC_TSR);

  read_myID();
  
  Wire.begin();

  pinMode(hydroPowPin, OUTPUT);
  pinMode(displayPow, OUTPUT);
  pinMode(sgtlEn, OUTPUT);

  pinMode(vSense, INPUT);
  analogReference(DEFAULT);

  digitalWrite(hydroPowPin, HIGH);
  digitalWrite(displayPow, HIGH);
  digitalWrite(sgtlEn, HIGH);

  
  //setup display and controls
  pinMode(UP, INPUT_PULLUP);
  pinMode(DOWN, INPUT_PULLUP);
  pinMode(SELECT, INPUT_PULLUP);
//  digitalWrite(UP, HIGH);
//  digitalWrite(DOWN, HIGH);
//  digitalWrite(SELECT, HIGH);  

  //setSyncProvider(getTeensy3Time); //use Teensy RTC to keep time
  t = getTeensy3Time();
  if (t < 1451606400) Teensy3Clock.set(1451606400);

  display.begin(SSD1306_SWITCHCAPVCC, 0x3C);  //initialize display
  delay(140);
  cDisplay();
  display.println("Loggerhead");
  display.display();


  pinMode(ledGreen, OUTPUT);
  digitalWrite(ledGreen, HIGH);

  cDisplay();
  display.println("Loggerhead");
  display.display();
  
  // Initialize the SD card
  SPI.setMOSI(7);
  SPI.setSCK(14);
  if (!(sd.begin(10))) {
    // stop here if no SD card, but print a message
    Serial.println("Unable to access the SD card");
    
    while (1) {
      cDisplay();
      display.println("SD error. Restart.");
      displayClock(getTeensy3Time(), BOTTOM);
      display.display();
      delay(1000);  
      //resetFunc();
    }
  }
  //SdFile::dateTimeCallback(file_date_time);
  LoadScript(); // secret settings accessible from the card
  manualSettings();
  
  // Audio connections require memory, and the record queue
  // uses this memory to buffer incoming audio.
  // initialize now to estimate DC offset during setup
  AudioMemory(MQ+10);
  
  audio_srate = lhi_fsamps[isf];
//WMXZ  audioIntervalSec = 256.0 / audio_srate; //buffer interval in seconds

  AudioInit(isf); // this calls Wire.begin() in control_sgtl5000.cpp

  logFileHeader();
  
  cDisplay();

  int roundSeconds = 10;//modulo to nearest x seconds
  if(rec_int > 60) roundSeconds = 60;
  if(rec_int > 300) roundSeconds = 300;
  
  t = getTeensy3Time();
  startTime = t;
  //startTime = getTeensy3Time();
  startTime -= startTime % roundSeconds;  
  startTime += roundSeconds; //move forward
  stopTime = startTime + rec_dur;  // this will be set on start of recording
  
 // if (recMode==MODE_DIEL) checkDielTime();  
  
  nbufs_per_file = (long) (ceil(((rec_dur * audio_srate / 256.0) / (float) NREC)) * (float) NREC);
  long ss = rec_int - wakeahead;
  if (ss<0) ss=0;
  snooze_hour = floor(ss/3600);
  ss -= snooze_hour * 3600;
  snooze_minute = floor(ss/60);
  ss -= snooze_minute * 60;
  snooze_second = ss;
  Serial.print("Snooze HH MM SS ");
  Serial.print(snooze_hour);
  Serial.print(snooze_minute);
  Serial.println(snooze_second);

  Serial.print("rec dur ");
  Serial.println(rec_dur);
  Serial.print("rec int ");
  Serial.println(rec_int);
  Serial.print("Current Time: ");
  printTime(t);
  Serial.print("Start Time: ");
  printTime(startTime);
  
  // Sleep here if won't start for 60 s
  long time_to_first_rec = startTime - t;
  Serial.print("Time to first record ");
  Serial.println(time_to_first_rec);
  
  mode = 0;

  // create first folder to hold data
  folderMonth = -1;  //set to -1 so when first file made will create directory
}

//
// MAIN LOOP
//

int recLoopCount;  //for debugging when does not start record
  
void loop() {
  // Standby mode
  if(mode == 0)
  {
      t = getTeensy3Time();
      cDisplay();
      display.println("Next Start");
      displayClock(startTime, 20);
      displayClock(t, BOTTOM);
      display.display();
      //
      //static uint32_t to; if(t >to) Serial.println(t); to=t;
      //

      if(t >= startTime){      // time to start?
        if(noDC==0) {
          audio_freeze_adc_hp(); // this will lower the DC offset voltage, and reduce noise
          noDC = -1;
        }
        Serial.println("Record Start.");
        
        stopTime = startTime + rec_dur;
        startTime = stopTime + rec_int;
      //  if (recMode==MODE_DIEL) checkDielTime();

        Serial.print("Current Time: ");
        printTime(getTeensy3Time());
        Serial.print("Stop Time: ");
        printTime(stopTime);
        Serial.print("Next Start:");
        printTime(startTime);

        mode = 1;
        display.ssd1306_command(SSD1306_DISPLAYOFF); // turn off display during recording
        startRecording();
      }
  }


  // Record mode
  if (mode == 1) {
    continueRecording();  // download data
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

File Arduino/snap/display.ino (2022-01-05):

float mAmpRec = 45;  // actual about 43 mA
float mAmpSleep = 2.8; // actual about 2.6 mA
byte nBatPacks = 1;
float mAhPerBat = 12000.0; // assume 12Ah per battery pack; good batteries should be 14000

uint32_t freeMB;
uint32_t filesPerCard;
csd_t m_csd;


/* DISPLAY FUNCTIONS
 *  
 */

time_t autoStartTime;
 
void printDigits(int digits){
  // utility function for digital clock display: prints preceding colon and leading 0
  display.print(":");
  printZero(digits);
  display.print(digits);
}

void printZero(int val){
  if(val<10) display.print('0');
}

#define noSet 0
#define setRecDur 1
#define setRecSleep 2
#define setYear 3
#define setMonth 4
#define setDay 5
#define setHour 6
#define setMinute 7
#define setSecond 8
#define setMode 9
#define setStartHour 10
#define setStartMinute 11
#define setEndHour 12
#define setEndMinute 13
#define setFsamp 14

void manualSettings(){
  boolean startRec = 0, startUp, startDown;
  Serial.print("Gain:");
  Serial.println(gainSetting);
  Serial.println("Read EEPROM");
  readEEPROM();
  calcGain();
  Serial.print("Gain:");
  Serial.println(gainSetting);

  autoStartTime = getTeensy3Time();

// get free space on cards

    cDisplay();
    display.print("Snap Init");
    display.setTextSize(1);
    display.setCursor(0, 16);
    display.println("Card Free/Total MB");
    
    freeMB = 0; //reset
    Serial.println(); Serial.println();
    Serial.print("Card:"); 
    display.display();
    
    // Initialize the SD card

    SPI.setMOSI(7);
    SPI.setSCK(14);
    SPI.setMISO(12);
  
    if(sd.begin(10, SD_SCK_MHZ(50))){
      sd.card()->readCSD(&m_csd);
      
      //uint32_t volFree = sd.FsVolume.freeClusterCount();
      uint32_t volMB = uint32_t ( 0.000512 * sdCardCapacity(&m_csd));    
      
      Serial.print("Volume (MB): ");
      Serial.println((uint32_t) volMB);

      if (volMB < 200) freeMB = 0;
      else
        freeMB = volMB - 200; // take off 200 MB to be safe
      
      display.print(freeMB);
      display.print("/");
      display.println(volMB);
      display.display();
    }
    else{
      Serial.println("Unable to access the SD card");
      //Serial.println(card.errorCode());
     // Serial.println(card.errorData());
      display.println("  None");
      display.display();
  }
  
  // make sure settings valid (if EEPROM corrupted or not set yet)
  
  if (rec_dur < 0 | rec_dur>100000) {
    rec_dur = 60;
    writeEEPROMlong(0, rec_dur);  //long
  }
  if (rec_int<0 | rec_int>100000) {
    rec_int = 60;
    writeEEPROMlong(4, rec_int);  //long
  }
  if (startHour<0 | startHour>23) {
    startHour = 0;
    EEPROM.write(8, startHour); //byte
  }
  if (startMinute<0 | startMinute>59) {
    startMinute = 0;
    EEPROM.write(9, startMinute); //byte
  }
  if (endHour<0 | endHour>23) {
    endHour = 0;
    EEPROM.write(10, endHour); //byte
  }
  if (endMinute<0 | endMinute>59) {
    endMinute = 0;
    EEPROM.write(11, endMinute); //byte
  }
  if (recMode<0 | recMode>1) {
    recMode = 0;
    EEPROM.write(12, recMode); //byte
  }
  if (isf<0 | isf>=I_SAMP) {
    isf = 4;
    EEPROM.write(13, isf); //byte
  }
  if (gainSetting<0 | gainSetting>15) {
    gainSetting = 4;
    EEPROM.write(14, gainSetting); //byte
  }


//  // if LOG.CSV present, skip manual settings
//  #if USE_SDFS==1
//    FsFile logFile = sd.open("LOG.CSV");
//  #else
//    File logFile = sd.open("LOG.CSV");
//  #endif
//  if(logFile){
//    startRec = 1;
//    logFile.close();
//  }
  
  while(startRec==0){
    static int curSetting = noSet;
    static int newYear, newMonth, newDay, newHour, newMinute, newSecond, oldYear, oldMonth, oldDay, oldHour, oldMinute, oldSecond;
    
    // Check for mode change
    boolean selectVal = digitalRead(SELECT);
    if(selectVal==0){
      curSetting += 1;
      while(digitalRead(SELECT)==0){ // wait until let go of button
        delay(10);
      }
      if(recMode==MODE_NORMAL & (curSetting>8) & (curSetting<14)) curSetting = 14;
      if(recMode==MODE_NORMAL & (curSetting>14)) curSetting = 0;
   }

    cDisplay();

    t = getTeensy3Time();
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

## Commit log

2016-10-03 stop recording if voltage < 3.0V
2016-10-03 remove unused sensor code. reset if can't write wav file
2017-01-06 swith from Wire library to i2c_t3
2017-01-06 going back to Wire.h because display libraries use internal Wire.h definitions
2017-01-13 set input to no gain; Left input only powered
2017-01-18 display off during record to eliminate noise. Removed unused sensor code:
2017-05-19 back to teensy RTC. now() is millis() based clock
2017-05-19 Teensy3Clock class wraps rtc_get and rtc_set
2018-05-10 update build for lower power sd firmware
2018-08-03 multiple sample rates
2018-08-20 change RTC load capacitance at startup
2018-08-30 updated hex
    Changes capacitance of RTC xtal
2018-09-17 update power calculation
2018-09-17 print diagnostics off
2018-09-18 comment print dots during acquire
    So OK if forget to turn printDiags off
2019-04-09 fix power draw on UP button
2019-06-04 reset if get bad voltage reading that comes back
    added hystersis to voltage reading
2019-07-22 titanium snap lithium metal
    [LSH20_LOG.CSV, LSH20_LOG2.CSV, LSS33600_LOG.CSV, LSS33600_LOG2.CSV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]
2019-09-17 Snap2 schematic
    [Snap2.PcbDoc, Snap2.PrjPCB, Snap2.SchDoc, Snap2_audio.SchDoc]
2019-09-17 PCB layout
    [Snap2.PcbDoc, Snap2.PrjPCB, Snap2.SchDoc, Snap2_audio.SchDoc]
2019-09-17 route power
    [Snap2.PcbDoc, Snap2.SchDoc, Snap2_audio.SchDoc]
2019-09-17 adjust silkscreen
    [Snap2.PcbDoc, Snap2.PrjPCB]
2019-09-18 move vias from Teensy area
    [Snap2.PcbDoc]
2019-12-17 Snap2 LED support
2022-01-10 diode option
    supply chain FUN!
    [Snap21.PcbDoc, Snap21.PrjPCB, Snap21.SchDoc, Snap21_audio.SchDoc]
2022-01-10 Snap2.1 add diode option
    [Pick Place for Snap21.csv, Snap2.21_BOM.xlsx, Snap21.GBL, Snap21.GBO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]
2022-01-13 fix via
    [Snap21.GBL, Snap21.GBO, Snap21.GBP, Snap21.GBS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]
2022-01-14 fix LDO pad solder mask
    [Snap21.GBL, Snap21.GBO, Snap21.GBP, Snap21.GBS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]
2022-12-12 Snap3 DS3231RTC
    microSD powered from separate voltage regulator
    [Snap3.PcbDoc, Snap3.PrjPCB, Snap3.SchDoc, Snap3_audio.SchDoc]
2022-12-12 smallest via 12mil
    [Snap3.PcbDoc, Snap3.PrjPCB]
2022-12-12 update caps on ADP1712 LDO
    [Snap3.SchDoc]
